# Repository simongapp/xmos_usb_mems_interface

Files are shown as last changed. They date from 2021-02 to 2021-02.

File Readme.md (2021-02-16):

# XMOS USB - MEMS microphone array audio interface
Hardware and firmware files for a MEMS microphones USB audio interface based on the XMOS XUF216. Allows to connect up to  16 microphones and provides the option to cascade multiple base boards.  

This work was done as part of my master's thesis at the TU Berlin, Department of Engineering Acoustics [https://www.akustik.tu-berlin.de/menue/home/parameter/en/](https://www.akustik.tu-berlin.de/menue/home/parameter/en/). The system was evaluated with the Acoular Framework for beamforming [http://www.acoular.org/](http://www.acoular.org/).

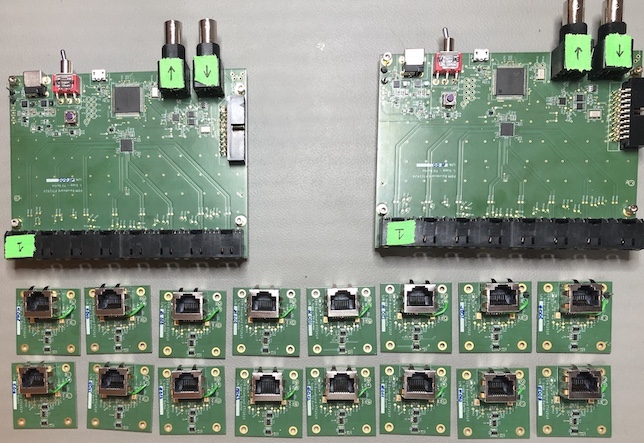
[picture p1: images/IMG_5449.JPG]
  

## Features
- Operates at 48kHz/24bit, with USB 2.0 (UAC2)
- One base board can process up to 16 MEMS microphones
- Cascade multiple baseboards by sharing a word clock or sync to external clock master
- Physically detached microphones, allows to add microphones in pairs of two
- Max. cable length between microphones and base board: 2.5m @ 48kHz
- Impedance matched clock and data transmission lines

## Folders
- 00PCB: EAGLE PCB files for the microphone PCBs and base board
- 01Firmware: XMOS firmware, port documentation and visualizations of the reference code

## Usage
- Clone to your local hard drive

- How to add the firmware files to xTimeComposer (based on https://gist.github.com/ahogen/93bf33ce47bb96c7fda60d844238fa43):  
  1. Link (but don't copy) projects and libraries from SVN dir into workspace
     1. File > Import > General > Existing Projects into Workspace
     2. Choose "Select root directory"
     3. Click "Browse" and navigate to the SVN dir where your projects and libraries were exported
     4. Click "Select All" to choose all projects and libraries
     5. Make sure "Copy projects into workspace" is not checked
     6. Finish

## Known issues
- Data transfer from the microphone boards to the base board leads to inverted data signals on the base board. Fixed by multiplying -1 on the PCM signals.
- No deterministic phase relationship between input and output of the CS2100. This results in a non-deterministic clock shift of up to 162.5ns@48kHz. Considered negligible with respect to the period of audio frequencies from 50ms(20Hz) to 42us(20kHz).
- The current firmware starts audio sampling as soon as the uC is ready, which leads to different buffer sizes and thus a delay of several samples at the host when using multiple base boards. Solution: Synchronize start of audio sampling to first SOF after device configuration. To be implemented in the future.

## License
MIT License

Copyright (c) 2021 Simon Gapp

Permission is hereby granted, free of charge, to any person obtaining a copy
of this software and associated documentation files (the "Software"), to deal
in the Software without restriction, including without limitation the rights
to use, copy, modify, merge, publish, distribute, sublicense, and/or sell
copies of the Software, and to permit persons to whom the Software is
furnished to do so, subject to the following conditions:

The above copyright notice and this permission notice shall be included in all
copies or substantial portions of the Software.

THE SOFTWARE IS PROVIDED "AS IS", WITHOUT WARRANTY OF ANY KIND, EXPRESS OR
IMPLIED, INCLUDING BUT NOT LIMITED TO THE WARRANTIES OF MERCHANTABILITY,
FITNESS FOR A PARTICULAR PURPOSE AND NONINFRINGEMENT. IN NO EVENT SHALL THE
AUTHORS OR COPYRIGHT HOLDERS BE LIABLE FOR ANY CLAIM, DAMAGES OR OTHER
LIABILITY, WHETHER IN AN ACTION OF CONTRACT, TORT OR OTHERWISE, ARISING FROM,
OUT OF OR IN CONNECTION WITH THE SOFTWARE OR THE USE OR OTHER DEALINGS IN THE
SOFTWARE.

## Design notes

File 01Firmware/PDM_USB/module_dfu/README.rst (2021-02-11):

module_dfu
==========

:scope: General Use
:description: module_dfu
:keywords: DFU
:boards: XMOS USB Audio Reference Designes

Code providing firmware upgrade over USB.

./host provides an example of a host application for DFU.  This is written and tested for OSX.  LibUSB is used to aid cross-platform porting.

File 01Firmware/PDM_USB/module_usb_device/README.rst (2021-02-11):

xCORE-USB Device Library
========================

:scope: General Use
:description: Library providing USB-device capabilities on xCORE-USB devices.
:keywords: usb, endpoint

The xCORE-USB Device Library provides support for creating USB devices on the
xCORE-USB family of devices. There are two demonstration applications for using
the library; a HID Class demo and a Custom Class demo.

The Design Guide for more information on using this library to create USB devices.

**Note:** this library can be used with the L-Series but the ``Makefile`` will
need to be modified as described in the Design Guide.

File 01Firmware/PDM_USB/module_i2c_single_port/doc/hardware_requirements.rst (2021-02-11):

Evaluation Platforms
====================

Recommended Hardware
--------------------

This module may be evaluated using the sliceKIT Modular Development Platform, available from digikey. Required board SKUs are:

   * XP-SKC-L16 (sliceKIT L16 Core Board) plus XA-SK-AUDIO plus XA-SK-XTAG2 (sliceKIT xTAG adaptor) plus xTAG-2 (debug adaptor)

Demonstration Application
-------------------------

Example usage of this module can be found within the xSOFTip suite as follows:

   * Package: sc_i2s
   * Application: I2S Master sliceKIT Loop back Demo

The module is used within this application to configure the codec on the Audio sliceCARD.

Hardware Requirements
=====================

This module requires 1K pull-up resistors be present on SCL and SDA externally.

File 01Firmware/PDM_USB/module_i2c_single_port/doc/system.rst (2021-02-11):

Overview 
========

I2C Component provides the ability to write and read I2C based slave devices.
It incorporates features like multimaster capability, clock stretching and clock synchronization.

Components 
----------

i2c master write
++++++++++++++++++++++++

i2c master write component writes the data into i2c slave devices.
 
i2c master read
+++++++++++++++++++++++

i2c master read component read the data from i2c slave devices.

Programming Guide 
=================
 
API (Application Programming Interface)
---------------------------------------

   int i2c_master_wr(int addr, int device, struct i2c_data_info &i2c_data, struct r_i2c &i2c_master);

   This function receives the device address of the slave, the internal address of the slave into which data has to 
   be written, structure containing information about the length of the data and the data itself and the structure 
   containing ports for scl and sda. The device address and the internal address and the data are serially transmitted 
   on sda line.

   int i2c_master_rd(int addr, int device, struct i2c_data_info &i2c_data, struct r_i2c &i2c_master);

   This function receives the device address of the slave, the internal address of the slave from which data has to 
   be read, structure to store the length of received data and the data itself and the structure 
   containing ports for scl and sda.  The device address and the internal address are sent serially and the data received 
   is stored in a structure.

Macros
------

   #define MASTER_TX : if used enables the MASTER Transmit. If commented enables the MASTER receive.

   #define MASTER1 : If used enables the MASTER1 in testbench and if commented disables the MASTER1.

   #define MASTER2 : If used enables the MASTER2 in testbench and if commented disables the MASTER2.

   #define SLAVE1  : If used enables the SLAVE1 in testbench and if commented disables the SLAVE1.

   #define SLAVE2  : If used enables the SLAVE2 in testbench and if commented disables the SLAVE2.

Resource Usage
==============

The following table gives the details of the memory foot print of the functions used.
   
 +----------------+------------------+
 |   function     |   Size(in Bytes) | 
 +================+==================+
 | i2c_master_tx  |       790        |  
 +----------------+------------------+			
 | i2c_master_rx  |       914        |
 +----------------+------------------+
 | i2c_slave_rx   |       584        |    
 +----------------+------------------+ 
 | i2c-slave_tx   |       526        |    
 +----------------+------------------+
 | wait_func      |        74        |
 +----------------+------------------+

Timing Constraints 
==================

I2C Master work at 400Kbps and below.

Validation 
==========
   
Test Bench is provided for testing I2C Master. Both I2C master read and write is tested.
i2C Master is tested for following features

1. Multimaster capability

2. Clock synchronization.

3. Clock stretching.

README.rst file provided guides to setup the simulation environment and the RESULT.rst file gives
the details of tests and the test results.

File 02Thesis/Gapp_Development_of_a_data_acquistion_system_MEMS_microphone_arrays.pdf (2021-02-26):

## berlin

# Masterarbeit Development of a data acquisition system specialized in MEMS microphone arrays

### erstellt von Simon Gapp Matrikel Nr.: 351468

### Erstprufer: Prof. Dr.-Ing. Ennes Sarradj ¨ Zweitprufer: Prof. Giuseppe Caire, Ph.D. ¨

Betreuer: | Dipl.-Ing. Gert Herold
| Dr.-Ing. Andreas Kortke

Technische Universit¨at Berlin, Fachgebiet Technische Akustik Institut fur Str ¨ ¨omungsmechanik und Technische Akustik

17. Dezember 2020

# Erkl¨arung

Hiermit erkl¨are ich, dass ich die vorliegende Arbeit selbstst¨andig und eigenh¨andig sowie ohne unerlaubte fremde Hilfe und ausschließlich unter Verwendung der aufgefuhrten Quellen und Hilfsmittel angefertigt habe. ¨

Berlin, den 17. Dezember 2020

Unterschrift

## Danksagung

Ich m¨ochte mich bei Prof. Sarradj vom Lehrstuhl fur Technische Akustik und bei ¨ Prof. Caire vom Fachgebiet Theoretische Grundlagen der Kommunikationstechnik
fur die M ¨ | ¨oglichkeit, dieses Thema zu bearbeiten zu k¨onnen, herzlich bedanken. Ein
ganz besonderer Dank geht an Gert Herold und Dr. Andreas Kortke fur alle Kom- ¨
mentare, Tipps und Tricks, praktische Unterstutzung sowie die ¨ | ¨außerst prompten
Antworten auf alle meine Anfragen. Weiterer Dank geht an Simon Jekosch fur die ¨ unkomplizierte Urlaubsvertretung und Torsten Daniel fur die handwerkliche Un- ¨
terstutzung beim Messaufbau sowie an das XCore exchange Forum f ¨ | ur alle meine ¨
XMOS Anf¨angerfragen.

1

## Abstract

This thesis describes the design process of a modular Data Acquisition System (DAQ) for Micro-Electro-Mechanical Systems (MEMS) microphone arrays.
Compared to condenser microphones, MEMS microphones come at a significantly lower price, have a smaller footprint, are more resistant towards aging and temperature influences and can contain an integrated Analog-to-Digital Converter (ADC). On the other hand, they have a smaller range with a flat frequency response and usually a lower sensitivity. This results in a lower Signal-to-Noise Ratio (SNR), which can be compensated by increasing the number of microphones and cross-correlating the data in post-processing.
Solutions based on MEMS microphones usually have a fixed array shape with a defined number of microphones. The modular approach of this thesis detaches the Digital Signal Processor (DSP) unit physically from the microphone part, making it possible to adjust the array form at any time. Furthermore, it is possible to cascade multiple DSP units, making the available Universal Serial Bus (USB) bandwidth the limiting factor of the system.

## Zusammenfassung

Diese Arbeit beschreibt den Entwurf eines modularen Data Acquisition System (DAQ) fur Micro-Electro-Mechanical Systems (MEMS)-Mikrofonarrays. ¨
Im Vergleich zu Kondensatormikrofonen sind MEMS Mikrofone deutlich preiswerter, haben einen geringeren Platzbedarf, sind resistenter gegen Alterung und Temperatu-
reinflusse und k ¨ | ¨onnen einen bereits integrierten Analog-to-Digital Converter (ADC)
enthalten. Auf der anderen Seite haben sie einen kleineren Bereich mit einem flachen Frequenzgang und meist eine geringere Empfindlichkeit. Daraus ergibt sich ein geringeres Signal-to-Noise Ratio (SNR), das aber durch eine gr¨ossere Anzahl von Mikrofonen und einer Kreuzkorrelation der Daten in der Nachbearbeitung kompensiert werden kann.
Bestehende L¨osungen, die auf MEMS Mikrofonen basieren, haben meist eine feste Array Form und eine definierte Anzahl von Mikrofonen. Der modulare Ansatz dieser Arbeit trennt die Digital Signal Processor (DSP) Einheit physisch vom Mikrofonteil, sodass eine Anpassung der Array Form jederzeit m¨oglich ist. Daruber hinaus ist es ¨ m¨oglich, mehrere DSP Einheiten zu kaskadieren, wodurch die verfugbare Universal ¨ Serial Bus (USB) Bandbreite zum begrenzenden Faktor des Systems wird.

2

# Contents

Erkl¨arung | 1
Abstract | 2
Zusammenfassung | 2
1 Introduction | 11
2 Operating principles | 14
3 Implementation | 77
4 Results | 103
5 Summary and future work | 124
Bibliography | 129

3

A PCB Files | 135
A.1 Microphone PCB schematics | 135
A.2 Microphone PCB Layout Top | 136
A.3 Microphone PCB Layout Bottom | 137
A.4 Base board schematics | 138
A.5 Base board Layout Top | 146
A.6 Base board Layout Bottom | 147
A.7 Base board Layout Power | 148
B Port Assignments | 149
C Test Points | 151
D CS2100 configuration | 152
E SpectAcoular Code | 153
E.1 Class pdm bb | 154
E.2 Microphone grid | 157
E.3 pdm bb.xml | 159

4

# List of Figures

2.1 Components of a PDM MEMS Microphone | | 15
2.2 Mechanical specifications of a top port MEMS transducer | | 16
2.3 Simplified model of a bottom port MEMS microphone | | 16
2.4 Typical frequency response of a MEMS microphone | | 17
2.5 Analog to digital data converter system | | 19
2.6 Spectrum of a sampling operation | | 20
2.7 Linear quantizer model | | 21
2.8 Quantization error according to the linear model | | 22
2.9 Spectral effect of oversampling | | 23
2.10 Block diagram of a first order Σ∆ ADC | | 24
2.11 Exemplary PDM output and sampled sinus with 64x oversampling . . | 25
2.12 Effect of noise shaping in the Σ∆ modulator | | 26
2.13 CIC decimation filter | | 27
2.14 Exemplary circuit for line termination | | 29
2.15 Exemplary single ended transmission | | 30
2.16 Exemplary differential transmission | | 31
2.17 Setup and hold timing | | 33
2.18 xCore hardware architecture | | 36
2.19 Descriptor relationship | | 47
2.20 Packet Identifier (PID) field | | 49
2.21 Start of Frame (SOF) packet | | 50
2.22 IN, OUT, SETUP packet | | 50
2.23 Data packet structure | | 51
2.24 Retransmission after lost ACK | | 51
2.25 Handshake packet | | 52
2.26 Control Transfer Setup stage | | 54
2.27 Control Transfer Data stage | | 54
2.28 Control Transfer Status stage | | 55
2.29 Isochronous transfer | | 56

5

2.30 Interrupt transfer | | 56
2.31 Bulk transfer | | 57
2.32 bmRequestType field for a SETUP packet | | 58
2.33 Exemplary length of two Configuration Descriptors with wTotalLength 64
2.34 USB Audio device structure using the AC and AS class | | 69
2.35 bmRequestType field for AC requests | | 70
2.36 Comparison of the IAD to the conventional approach | | 76
3.1 Top level view of the system | | 78
3.2 Microphone PCB block diagram | | 79
3.3 Top level view of the base board | | 83
3.4 Clock Generation part of the base board | | 85
3.5 Impedance matching for external clock master | | 88
3.6 Top level view of the main XUF216 tasks | | 88
3.7 Multilayer structure of the used PCB | | 90
3.8 Clock and data path of the system | | 92
3.9 Timing diagram for the base board | | 93
3.10 Core usage and communication between cores | | 95
3.11 Project structure | | 96
3.12 Sixteen count PDM interface | 100
3.13 Frequency response of the decimator | 102
4.1 Manufactured base boards and microphone PCBs | 104
4.2 Measurement setup for a single base board | 105
4.3 Audio master clock on the base board | 106
4.4 Transmitted and received clock signals | 107
4.5 Data signals on the receiving base board | 109
4.6 Setup for the cascaded base board measurement | 110
4.7 Jitter measurement of the 12.288 MHz clocks | 111
4.8 Microphone spacing | 112
4.9 Microphone array layout | 113
4.10 Block diagram of the measurement setup | 114
4.11 Impressions of the measurement | 115
4.12 Measurement positions | 116
4.13 Cross-correlation for adjacent microphones at an incidence angle of 40.5°117
4.14 Frequency response of the microphones normed at 1 kHz | 118
4.15 Delay in samples between base boards, relative to fS = 48 kHz . . . . 120 4.16 Beamforming results. Orange dot: actual source position, pink dot:
estimated position | 122

6

# List of Tables

2.1 Pin assignment of the CAT6/RJ45 connector | | 29
2.2 Default kind for different pointer types | | 42
2.3 USB packet types | | 49
2.4 Setup packet details | | 58
2.5 Standard Requests for USB 2.0 | | 59
2.6 Format of the Device Descriptor | | 61
2.7 Available Languages ID String Descriptor, addressed with ID 0 . . . . | 63
2.8 String Descriptor, addressed from ID 1 and above | | 63
2.9 Configuration Descriptor format | | 65
2.10 Interface Descriptor format | | 66
2.11 Endpoint Descriptor format | | 67
2.12 Standard AudioControl Interface Descriptor | | 71
2.13 AudioControl Interface Header Descriptor | | 72
2.14 AudioControl Clock Source | | 72
2.15 Input Terminal Descriptor | | 73
2.16 Feature Unit Descriptor | | 74
2.17 Standard AudioStreaming Interface Descriptor | | 75
2.18 Class specific AudioStreaming Interface Descriptor | | 75
2.19 Interface Association Descriptor format | | 76
3.1 Current estimation of the system, measured values in brackets . . . . | 78
3.2 Current estimation for the microphone PCB, measured value in brackets 81
3.3 Sparrow limit of the validation array | | 81
3.4 Current estimation for the base board, measured value in brackets . . | 84
3.5 Mandatory components of the XMOS USB subsystem [68] | | 94
3.6 Core usage on Tile 0 | | 94
3.7 Core usage on Tile 1 | | 94
3.8 Description of used modules and libraries | | 96

7

4.1 Microphone PCB positions and corresponding IDs | 112
4.2 Measurement positions | 116
4.3 Used beamformer parameters | 121
4.4 Angular difference between the actual and calculated source position
for a delay of 10 sample | 123

8

## List of abbreviations

AC AudioControl

ACK Acknowledgement

ADC Analog-to-Digital Converter

AoIP Audio over IP

AOP Acoustic Overload Point

AS AudioStreaming

ASIC Application Specific Integrated Circuit

AVB Audio Video Bridging

CIC Cascaded-Integrator-Comb

COTS Commercial off-the-shelf

CRC Cyclic Redundancy Check

CS Control Selector

DAC Digital-to-Analog Converter

DAQ Data Acquisition System

dB Decibel

dBFS Decibel Full Scale

dBSPL Decibel Sound Pressure Level

DC Direct Current

DFU Device Firmware Upgrade

DMA Direct Memory Access

DSP Digital Signal Processor

ECL Emitter-coupled Logic

EMF Electromagnetic field

EOP End of Packet

ESD Electro Static Discharge

FFT Fast Fourier Transformation

FIFO First in, First out

FIR Finite Impulse Response Filter

FPGA Field-Programmable Gate Array

FU Feature Unit

GPIO General Purpose Input Output

GUI Graphical User Interface

HID Human Interface Device

HPF High-Pass Filter

ID Identifier

I/O Input/Output

IAD Interface Association Descriptor

IBN In-Band Noise

IC Integrated Circuit

IDE Integrated Development Environment

IFFT Inverse Fast Fourier Transformation

IIR Infinite Impulse Response Filter

9

ITD Input Terminal Descriptor

LDO Low Drop-out

LLVM Low Level Virtual Machine

LPF Low-Pass Filter

LSB Least Significant Bit

LVDS Low Voltage Differential Signaling

MEMS Micro-Electro-Mechanical Systems

MIPS Million Instructions Per Second

MIPS Million Instructions per Second

MSB Most Significant Bit

NRZI Non-return-to-zero, inverted

NTF Noise Transfer Function

OSR Oversampling Ratio

PCB Printed Circuit Board

PCM Pulse-Code Modulation

PDF Probability Density Function

PDM Pulse-Density Modulation

PECL Positive Emitter-coupled Logic

PHY Physical Layer

PID Packet Identifier

PLL Phase-Locked Loop

PSD Power Spectral Density

PSU Power Supply Unit

PTP Precision Timing Protocol

RTOS Real-Time Operating System

S-FTP Screen Foiled Twisted Pair

SHARC Super Harvard Architecture Single-Chip Computer

SNR Signal-to-Noise Ratio

SOF Start of Frame

SPST Single Pole Single Throw

STF Signal Transfer Function

THD Total Harmonic Distortion

TP Test Point

TSN Time Sensitive Networks

UAC1 Universal Serial Bus (USB) Audio Class 1.0

UAC2 USB Audio Class 2.0

USB Universal Serial Bus

VHDL Very High Speed Integrated Circuit Hardware Description Language

XUD XMOS USB Device Driver

10

# Chapter 1

# Introduction

A microphone array consists of several microphones placed in different locations. Typical applications of microphone arrays are speech extraction in noisy environments [1, 2] or source localization [3] often in combination with noise measurements [4]. Noise measurement applications usually consist of a larger number of microphones compared to speech extraction applications. Since the focus of this thesis is on a larger number of microphones, the introduction to this topic will be explained using examples from the field of noise measurements based on [5].
Typical measurement scenarios are in wind tunnels, during aircraft overflights and engine noise tests.
Depending on the goal of the measurement, various parameters can be adjusted, which are presented below.
The Signal-to-Noise Ratio (SNR) and the spatial resolution are defined by the microphone count. In general, it can be said that an increased number of microphones increases both, the SNR and the spatial resolution. The dynamic range, the frequency range and the sensitivity can be roughly approximated by the dimensions of a microphone. As a rule of thumb, it can be said that smaller microphones can measure higher frequencies compared to a larger microphone that usually has a higher sensitivity. The most accurate results can be achieved if the Data Acquisition System (DAQ) samples all microphones coherently.
Arranging the microphones in spirals or several circles with an odd number of regularly spaced microphones seems to give the best results.
Considering all hardware requirements, adequate results depend on the chosen algorithm. In general, the selection of the most suitable algorithm is a trade-off between spatial resolution, dynamic range and computational effort.

11

Microphone arrays based on Micro-Electro-Mechanical Systems (MEMS) microphones provide a cost-effective alternative to established systems based on condenser microphones. Advantages of the MEMS technology are a small footprint, low cost and a high resistance to aging and temperature influence. The microphones have, on the other hand, a smaller area with a flat frequency response due to their physical design and a lower SNR.

Commercially available arrays with up to 16 microphones are provided by [6, 7, 8]. Larger arrays are commercially available from [9]. Research projects on large scale arrays can be found in [10, 11, 12].
This thesis distinguishes between different processing stages with the terms preprocessing and post-processing. Preprocessing describes the conversion of the raw microphone signals into suitable signals for post-processing. Post-processing describes the application of an algorithm to evaluate the preprocessed microphone signals. All works presented apply preprocessing in a Digital Signal Processor (DSP) which is either a specialized microcontroller, a Field-Programmable Gate Array (FPGA) or an Application Specific Integrated Circuit (ASIC). In most of the works presented, post-processing is carried out on the same platform on which the preprocessing is performed.

A modular system is designed in this thesis in which the microphones are separated from the processing unit. The preprocessing is performed in the processing unit, while the post-processing is performed on an external device. The system consists of two physically separate units: the base board, which contains the processing unit as well as the peripherals necessary for its operation, and microphone Printed Circuit Boards (PCBs), which contain two microphones each as well as some peripherals necessary for their operation.
The term modular describes two aspects: Firstly, the possibility of operating a variable number of microphones with one processing unit and, secondly, the possibility of operating several processing units with the same clock signal for audio sampling. This overcomes the limitation of the ability to use only a single processing unit and the available transmission bandwidth becomes the limiting factor. Furthermore, the shape of the microphone array can be adjusted at any time.
In this thesis the following questions are evaluated:
- Does the modular system provide sufficiently accurate data for post-processing?
- Is it feasible to physically detach the microphones from the DSP?
- Is the selected transmission protocol suitable for transferring the array data?

12

## 1.1 Chapter overview

This thesis is divided into five chapters, covering the theoretical principles, the description of the design process and the subsequent validation of the developed system. It concludes with a summary of the work and presents suggestions for future implementations. The chapters are structured as follows:

Chapter 1 Introduces the topic and presents the research questions.

Chapter 2 Presents the operating principles of the microphones used and describes the review process for a suitable processing unit. Subsequently, details on the architecture of the selected processing unit are described. A further chapter is dedicated to the transmission protocol between a host and the processing unit and deals with the specific parts of the Universal Serial Bus (USB) protocol used in this work.

Chapter 3 Describes the implementation process for the hardware and the firmware.

Chapter 4 Provides details on the validation process of the system from an electrical and acoustic point of view.

Chapter 5 Summarizes this thesis, presents an answer to the research questions and provides suggestions for future implementations.

13

# Chapter 2

# Operating principles

This chapter presents the operating principles of the hardware and firmware that is used in this thesis. It is structured as follows: Sec. 2.1 reviews the principles that are used in a Micro-Electro-Mechanical Systems (MEMS) transducer. In Sec. 2.2, a brief review of the applied transmission techniques are presented. Sec. 2.3 describes the selection process of a suitable processing unit and Sec. 2.4 describes the architecture of the selected unit in more detail. Lastly, Sec. 2.5 summarizes the relevant parts of the selected Universal Serial Bus (USB) protocol.

## 2.1 Data acquisition

The used microphones are based on the MEMS technology. As illustrated in Fig. 2.1, the two main components of the microphone are a MEMS transducer and a Σ∆ Analog-to-Digital Converter (ADC). Components other than the MEMS transducer are summarized below by the term Application Specific Integrated Circuit (ASIC).

### 2.1.1 Micro-Electro-Mechanical Systems transducer

This section describes the MEMS transducer principles based on [13, 14]. The transducer can be described as a silicon capacitor consisting of two plates. While one plate is at a fixed position, the other plate is moving accordingly to the pressure change caused by a sound wave. One could describe the MEMS transducer as a capacitor with variable capacitance. The capacitance of a plate capacitor is calculated as follows:

C = ε0εr

A
d

(2.1)

14

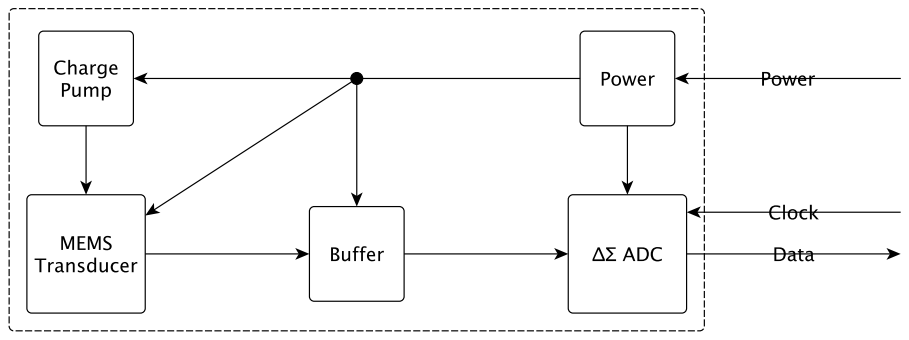
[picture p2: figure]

Figure 2.1: Components of a PDM MEMS Microphone, Figure from [13]

With A: Plate surface, d: Distance between plates, ε0: vacuum permittivity and εr: relative permittivity. By changing the distance of the two plates, a change in capacity is achieved, which results in a change in voltage:

U =

Q
C

(2.2)

With U: voltage, Q: charge and C: capacitance. The voltage change is detected by the buffer between the transducer and the Σ∆ ADC.

The mechanical specification for a top port MEMS microphone is depicted in Fig. 2.2. Sound waves enter from the top and pass the acoustic holes. The change in pressure causes the membrane to move, which eventually leads to a change in the capacitance of the transducer. This leads to a change in the charge of the capacitor plates, changing the input voltage at the ASIC.
Fig. 2.3 depicts a simplified model of a bottom port MEMS microphone with the ASIC and the enclosure. A bottom port microphone is also used in this thesis. The back volume is defined by the dimensions of the enclosure and the components placed inside, while the front volume is defined by the dimensions of the underlaying substrate.

15

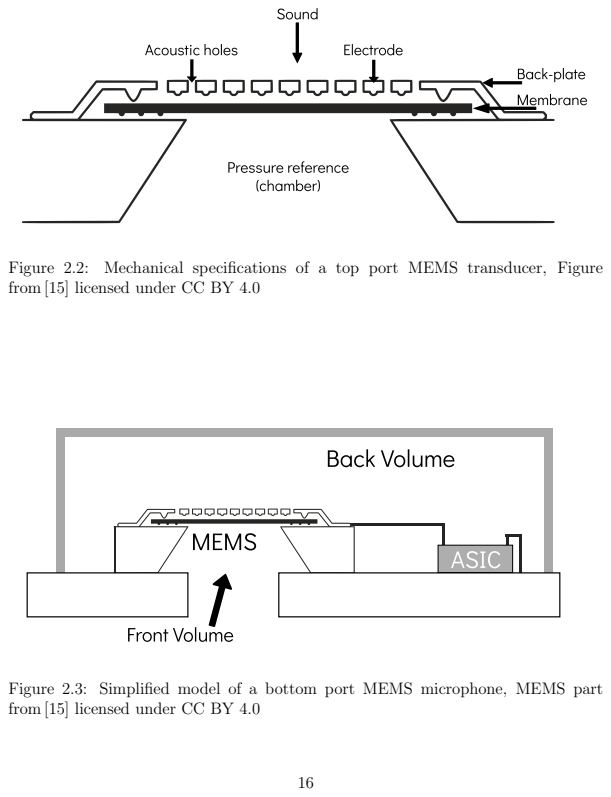
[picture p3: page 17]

Figure 2.2: Mechanical specifications of a top port MEMS transducer, Figure
from [15] licensed under CC BY 4.0

Figure 2.3: Simplified model of a bottom port MEMS microphone, MEMS part

The typical frequency response of a MEMS microphone as shown in Fig. 2.4. Two areas show a larger deviation from a flat frequency response: In the low frequency range from 10 Hz to 200 Hz and in the high frequency range above 10 kHz.

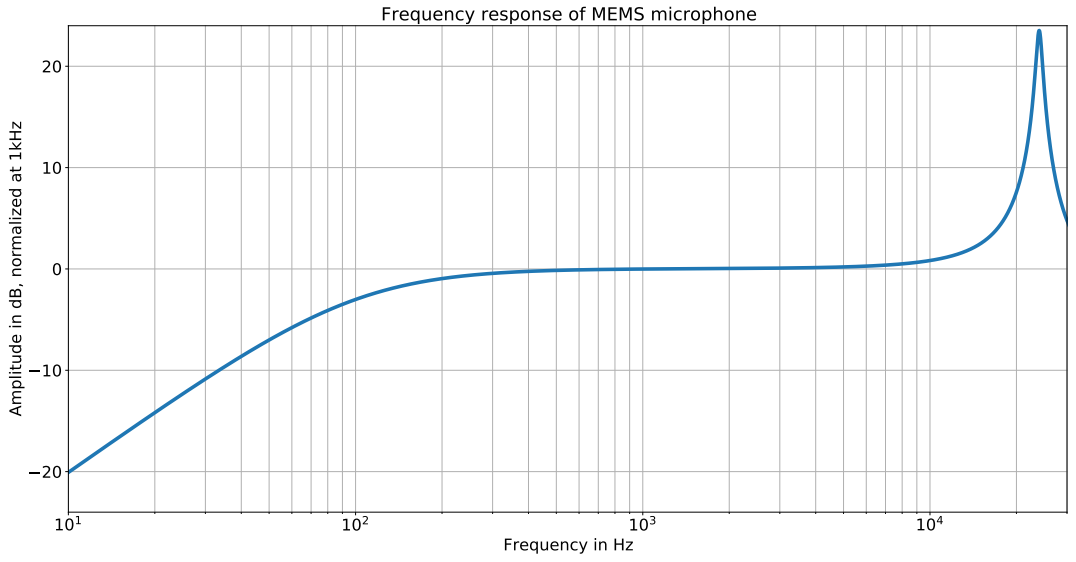
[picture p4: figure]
Frequency in Hz; Amplitude in dB, normalized at 1kHz; Frequency response of MEMS microphone

Figure 2.4: Typical frequency response of a MEMS microphone, Figure from [13]

These deviations are defined by the physical properties of the microphone. The main parameters are the form and size of the ventilation hole, the front chamber geometry and the back chamber geometry. It can be assumed that the ASIC has a flat frequency response.
While the attenuation at low frequencies is influenced by the geometry of the ventilation hole and the back chamber geometry, the gain at high frequencies is only influenced by the geometry of the front chamber. The high frequencies are amplified by a resonance peak caused by the Helmholtz effect. This effect describes the air resonance in a cavity. The resonance frequency is approximated as follows: [16]:

fR ≈

c
2π

r
S

V · Leff

(2.3)

With c: speed of sound, S: cross-section of the neck, V : volume of the back chamber and Leff: effective length of the neck which uses a correction factor of ∆l = 0.85r, with r: radius of the tube. The correction factor takes the effects at an open flange tube into account.

17

This approximation does not account for effects such as thermal-viscous and acoustic impedances and other material-related influences. Therefore, an approximate calculation of the resonance frequency for the microphone used is omitted.

### 2.1.1.1 Acoustic parameters

A microphone can be described with the following parameters:

Sensitivity The sensitivity of a digital microphone describes a percentage of the full scale output that is generated at 94 dBSPL. The value is given in Decibel Full Scale (dBFS) where the maximum value describes the highest signal level that can be output by the microphone. It is calculated as follows [17]:

SensitivitydBFS = 20 · log10 Sensitivity%FS

OutputDREF
(2.4)

With OutputDREF = 1.0. There is no relation between the digital output in dBFS and an analog output in dBV. The analog output is referenced to 1 VRMS while the digital output is referenced to the digital full scale.

Directivity The directivity of a microphone describes the variation of the sensitivity response with respect to the direction of arrival of the sound [14]. The MEMS transducer used is a pressure transducer and has an omnidirectional characteristic. This means that the sensitivity is independent from the location of the sound source and therefore identical for all locations.

Signal-to-Noise Ratio The Signal-to-Noise Ratio (SNR) specifies the ratio between a given reference signal (usually 1 kHz at 94 dBSPL) to the amount of residual noise at the microphone output [14].
The main contributor of the noise is the MEMS sensor while the noise of the ASIC can be neglected. The SNR is specified in Decibel (dB) and calculated as follows [18]:

SNR = 10 · log10

PSignal

PNoise

[dB] | (2.5)

Dynamic range The dynamic range describes the difference between the minimum and maximum signal the microphone is able to generate as an output. While the minimum signal describes the signal distinctive from residual noise, the maximum audio signal is described by the microphone output with 10 % Total Harmonic Distortion (THD) at 1 kHz. This point is known as Acoustic Overload Point (AOP).

18

### 2.1.2 Analog to digital conversion

The description of the analog to digital conversion is based on [18]. The basic principles of the analog to digital conversion can be separated into two main tasks:

- Uniform sampling in time
- Uniform quantization in amplitude

Fig. 2.5 depicts the main components of an ADC. It consists of three operating blocks: an antialiasing filter, a sample and hold block and a quantizer.

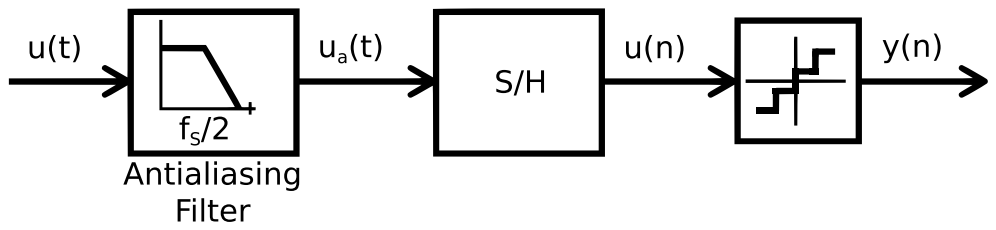
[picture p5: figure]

Figure 2.5: Analog to digital data converter system, Figure from [18]

With the following assumptions, it can be said that sampling in time is a completely invertible process: The signal information of the continuous input waveform u(t) is contained in the signal band |fsig| ≤ fB where fB is defined as the signal bandwidth. The input signal is sampled at uniform time intervals TS or with a fixed frequency fS, resulting in a periodicity of the original spectrum at multiples of fs. This is illustrated in Fig. 2.6.
The periodization arises from the sampling process which is considered as a multiplication of the input signal u(t) with a train of Dirac pulses spaced at 1/fs in the time domain or the convolution of the signal spectrum with a periodic train of Dirac pulses spaced at fs in the frequency domain. It can be seen in Fig. 2.6 that the original baseband spectrum can be reconstructed if the Nyquist theorem is fulfilled:
fs ≥ 2 · fB = fN | (2.6)

with fN as Nyquist frequency. This avoids overlapping and aliasing of the baseband. To only convert the bandwidth defined in Eq. 2.6, an antialiasing filter precedes the ADC.

19

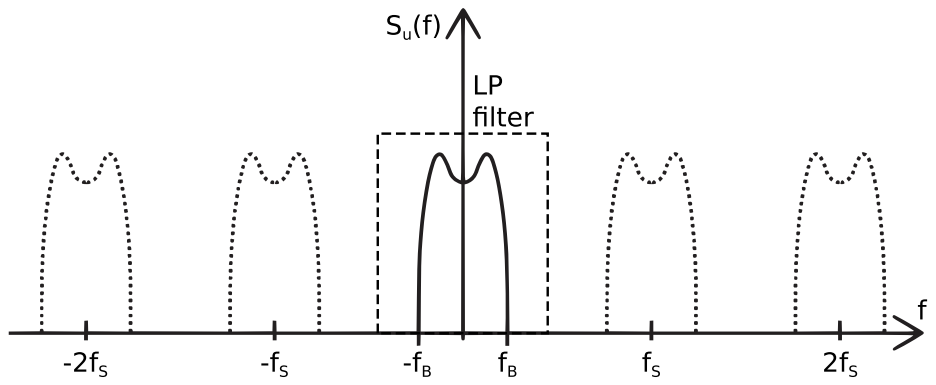
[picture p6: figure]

Figure 2.6: Spectrum of a sampling operation, Figure from [18]

Operating an ADC at the Nyquist frequency would result in zero transition band for the antialiasing filter to cut-off unwanted frequencies in the baseband.
Filters with a gentle roll-off are easier to design with the advantage that they require less power and introduce less phase distortion. Therefore, many ADCs work with sampling rates higher than fN . This is known as oversampling, hence the name oversampling ADCs. The Oversampling Ratio (OSR) is defined as:

OSR = fs 2 · fN
(2.7)

Converting a continuous range of analog values into a set of discrete levels is called quantization. This is a non-invertible process, since an infinite number of input amplitude values of the sampled analog signal u(n) are mapped into a finite number of output amplitude values. Even an ideal quantizer introduces an error into the output of the ADC.
The key characteristic of a quantizer is the number of Bits Bint which correlate to the different output levels. Mapping the analog input to 2Bint discrete output levels describes the resolution of the quantizer in terms of Bint-bits.
Assuming equally spaced levels, the quantizer operation is called uniform and has the following step width:

∆ = F S
2

Bint − 1

(2.8)

with F S: full-scale output range. The valid quantizer input range is from ±F S/2 which is quantized into 2Bint different output levels, encoded into a binary digital

20 representation. The resulting quantization error is defined as the difference between the input signal and the output signal.
The gain of a single bit quantizer is not exactly defined as well as the quantization error itself. Assuming the input changes rapidly from sample to sample by amounts larger than the step size ∆, then the quantization error appears uncorrelated and has an equal probability of lying anywhere in the range of [−∆/2, ∆/2]. This makes the assumption possible that the quantization error can have statistical properties. These properties define the basis of the additive white noise model of the quantizer which states that
- the quantization error can be expressed as a random variable.
- there is no correlation between the quantization error sequence e(n) and the input q(n).
- over the range [−∆/2, ∆/2], the Probability Density Function (PDF) of the quantization error process pdfe

is uniform.

- the Power Spectral Density (PSD) of the quantization error process Se(f) is flat

The linearized quantizer model is shown in Fig. 2.7. It represents the Input/Output (I/O) characteristics of the quantizer: a gain kq and a quantization error e(n).

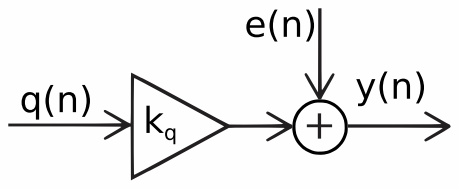
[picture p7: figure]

Figure 2.7: Linear quantizer model, Figure from [18]

These assumptions convert the deterministic nonlinear system into a stochastic linear system with the quantization error described as quantization noise. The total quantization noise power can be calculated from Fig. 2.8(a) as follows:

σ

2
e =

Z ∞

−∞

e

2
pdfe∂e =

∆²
12

(2.9)

21

It is independent from the sampling frequency and is only determined by the quantizer resolution. The signals at the quantizer are sampled signals, which causes all quantization noise power σ

2
e

to be folded into the frequency range of [−fS/2, fS/2]. Using white noise as an approximation (compare to Fig. 2.8(b)) results in the PSD of the quantizer being:

Se(f) = ∆²
12

1
fS

(2.10)

This means that the PSD reduces proportionally with an increased sampling frequency.

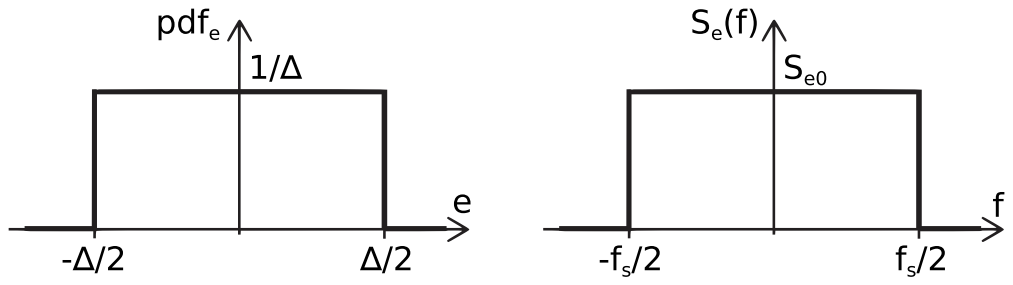
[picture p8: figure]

(a) Probability density function | (b) Power Spectral Density (PSD)

Figure 2.8: Quantization error according to the linear model, Figure from [18]

A digital low-pass filter follows the oversampled converter and eliminates all parts outside the in-band range, also leaving only a small part of the total quantization noise. The In-Band Noise (IBN) can be described as:

IBNOSR =

# Z fB

−fB

Se(f)df =

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
OSR | (2.11)

The maximum SNR of the ADC is described by the ratio between the corresponding input signal power PFS/2 and the IBN:

SNROSR = 10 · log10
PFS/2

IBNOSR
(2.12)

= 6.02 · Bint + 10 · log10 OSR + 1.76[dB]

Every doubling of the OSR increases the resolution by 3 dB or approx. 0.5 bit. The advantage of an increased OSR is depicted in Fig. 2.9.

22

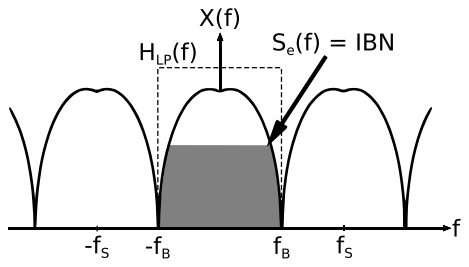
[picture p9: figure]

(a) Quantization and in-band noise for OSR=1

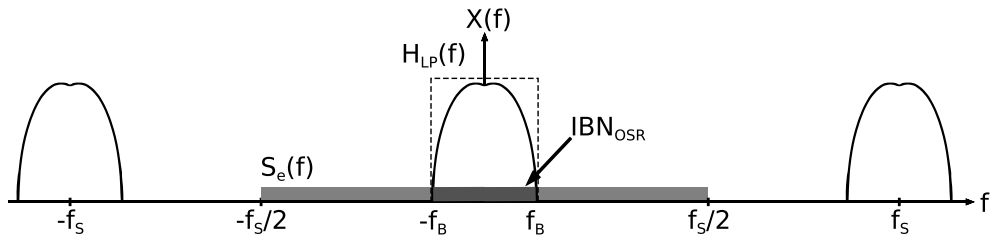
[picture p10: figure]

(b) Quantization and in-band noise for OSR=4

Figure 2.9: Spectral effect of oversampling, Figure from [18]

All theory until now was based on a purely open-loop controlled system. This means that the output signal is steered by an input signal and affected by noise introduced through the conversion process.

### 2.1.2.1 Σ∆ modulation

By introducing a feedback path to the system, a closed control loop is achieved. This makes it possible to implement different transfer functions and divide the output into a Signal Transfer Function (STF) and Noise Transfer Function (NTF).
In an ideal system, the configuration of the STF and the NTF leads to a complete cancelation of the noise inside the desired signal bandwidth, with the signal itself being unaffected. Outside the bandwidth of interest, the NTF gain can be high while the STF gain can be low.

NTFideal = STFideal =

(
0, −fB ≤ f ≤ fB
1, else

(2.13)

23

It is shown in Eq. 2.13 that the ideal STF is described by an ideal Low-Pass Filter (LPF), while the ideal NTF is described by an ideal High-Pass Filter (HPF) with the cut-off frequency being at least at fB. This results in the quantization noise being shaped away from the bandwidth of interest, leading to a noise shaping converter. The block diagram of a first order noise shaping converter is depicted in Fig. 2.10. Higher order noise shaping converters contain multiple integrator stages in the Σ∆ modulator block, which mainly increases the SNR.

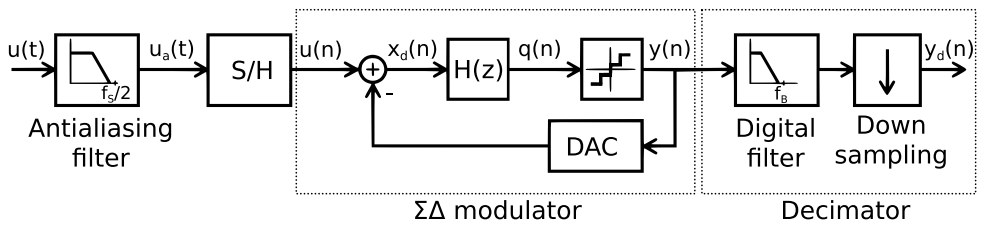
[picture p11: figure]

Figure 2.10: Block diagram of a first order Σ∆ ADC, Figure from [18]

A noise shaping converter consists of the following parts:

- Antialiasing Filter: The antialiasing filter eliminates spectral components above fs/2 which leads to a band limited input for the modulator. This filter ensures that the subsequent sampling operation does not alias input signals from higher frequencies into the band of interest
- Sample and Hold: The sample and hold block performs a track and hold operation. The function of this block can be described best as a clocked switch that charges a capacitance with the input for half of the clock period and transfers this voltage level from the capacitor to the Σ∆ modulator during the other half of the period. Eventually, it is interpreted by the quantizer.
- Σ∆ modulator: This block performs the actual analog to digital conversion by quantizing the input signal. Furthermore, the quantization error from the internal quantizer is moved out of the band of interest. The quantizer is typically implemented with a low resolution and the internal feedback Digital-to-Analog Converter (DAC) has the same resolution, thus not introducing additional error to the system. The output of the Σ∆ modulator is a Pulse-Density Modulation (PDM) signal.
A simulation of a sinusoidal input to a Σ∆ modulator is shown in Fig. 2.11. It

24 was created with the Delsig Toolbox [19] and shows that the density of zeros and ones is determined by the amplitude of the sine wave.

- Decimator: The decimation filter contains a digital low-pass filter to eliminate all noisy out of band components and performs the downsampling operation. A detailed description of the decimation process is presented in Sec. 2.1.2.2.

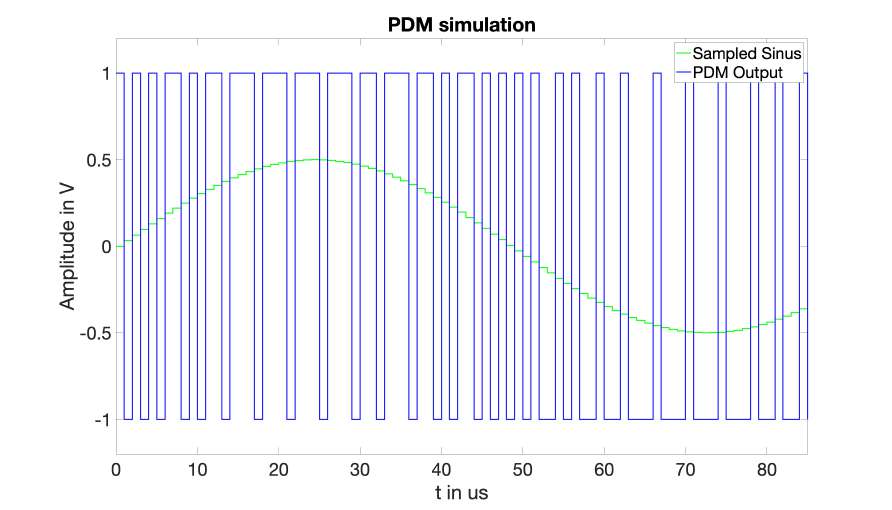
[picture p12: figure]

Figure 2.11: Exemplary PDM output and sampled sinus with 64x oversampling

Replacing the quantizer in Fig. 2.10 with the linearized quantizer model from Fig. 2.7 results in a linearized Σ∆ modulator with the following transfer function:

Y (z) = STF(z)U(z) + NTF(z)E(z) | (2.14)

with

STF(z) = 1

1
H(z)kq

+ 1

, NTF(z) = 1
1 + H(z)kq

(2.15)

and U(z): input signal, Y (z): output signal, U(z): quantization error.
The easiest filter for H(z) is a first order integrator described by the following transfer

25

function:

I(z) = z

−1
| 1 − z

−1

(2.16)

For low frequencies, the linearized Σ∆ modulator from Eq. 2.15 becomes:

STF(z) = z

−1
, NTF(z) ≈

1 − z

−1
kq

(2.17)

The effect of the high-pass filtered noise of the NTF is shown in Fig. 2.12. It is clearly visible that most of the noise is shaped out of the band of interest.

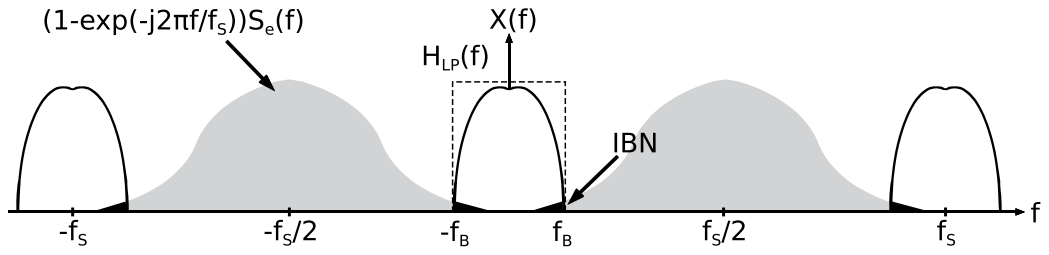
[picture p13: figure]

Figure 2.12: Effect of noise shaping in the Σ∆ modulator, Figure from [18]

The IBN can be approximated as follows:

IBN ≈

# Z fB

−fB

∆²
12fs

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
df | (2.18)

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
qOSR³

Increasing the oversampling ratio decreases the IBN power by 9 dB per octave. The corresponding SNR is approximated as follows:

SNR = 10 · log10
PSig
IBN1
∼ 10 · log10

OSR³
[dB] | (2.19)

This corresponds to 1.5 bit increase in resolution for doubling the OSR.

26

### 2.1.2.2 PDM to PCM conversion

For further signal processing the PDM signal from the Σ∆ modulator is converted into a Pulse-Code Modulation (PCM) signal which is suitable for post-processing. The two signal types are distinguished by their sampling rate and their bit-depth. The PDM signal has a high sampling rate and a low bit depth, while the PCM signal has a low sampling rate and a high bit-depth.
The decimation from a high sampling frequency to a low sampling frequency is performed by a Cascaded-Integrator-Comb (CIC)-Filter [20]. The filter structure is shown in Fig. 2.13. The filter is divided into two different structures: The integrator

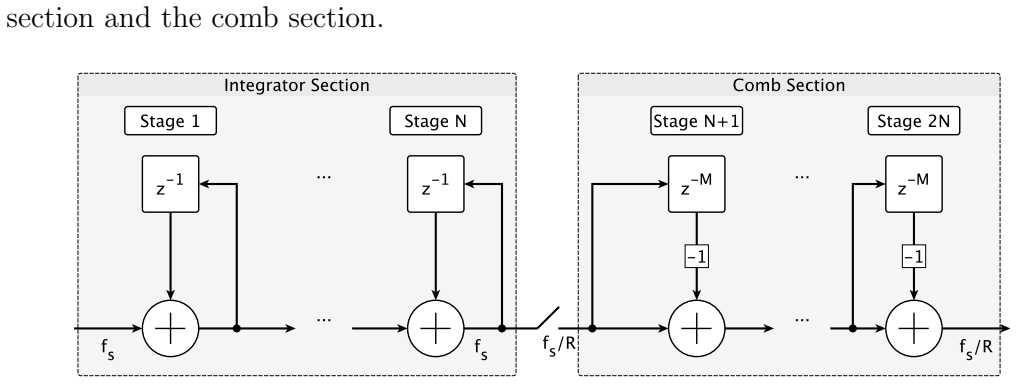
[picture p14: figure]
section and the comb section.

Figure 2.13: CIC decimation filter, Figure from [20]

The integrator section consists of N ideal digital integrator stages which operate at the high sampling frequency fS. Each stage is implemented as a one-pole filter with a unity feedback coefficient. The transfer function for a single integrator stage is [20]:

HI (z) = 1
1 − z

−1

(2.20)

The comb section operates at the low sampling rate fS/R. The integer R describes the rate change factor . The section consists of N comb stages with a differential delay of M samples per stage. This parameter is used to control the frequency response of the filter. The transfer function for a single comb stage is [20]:

HC(z) = 1 − z

−RM | (2.21)

The switch between the two stages subsamples the output of the last integrator stage. This reduces the sampling rate from fS to fS/R. The transfer function for

27 the complete CIC-Filter is [20]:

H(z) = H

N
I

(z)H

N
C (z) =
1 − z

−RMN

(1 − z

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
(2.22)

With R: Input sampling rate to output sampling rate ratio, M: number of samples per stage (usually 1 or 2) and N: Number of stages in the CIC-Filter.
Eq. 2.22 shows that the CIC-Filter is functionally equivalent to a cascade of N uniform FIR filter stages. This shows the advantage of the filter structure: The CIC-Filter does not need a multiplication unit since there are no coefficients other than ±1 which can be easily processed with a signed binary representation. Furthermore, it uses limited storage which results in a very economic hardware implementation. The frequency response is fully determined by the parameters R, M and N which limits the range of filter characteristics. It is recommended to use conventional filter structures to shape the frequency response after the CIC-Filter in the lower sampling rate domain where the number of multiplications per second is low.

The analog to digital conversion that is used in this project is divided into two stages. The MEMS microphone contains the Σ∆ modulator and sends the modulated data to the Digital Signal Processor (DSP) unit. In the DSP unit, the decimation of the signal is performed. This approach allows to specify the bit depth and sampling rate of the decimated PDM signal at runtime.

## 2.2 Data transmission

The microphones are physically separated from the processing unit. To ensure reliable transmission of the signals, the propagation velocity of the signals and the delay caused by the components used must be taken into account. This limits the maximum distance between the microphones and the processing unit.
The clock and data transmission are carried out over a distance of 2 m. In order to make the transmission reliable and less susceptible to external influences, the Low Voltage Differential Signaling (LVDS) principle is used for all transfers between the Printed Circuit Board (PCB)s.

28

All transmissions utilize CAT6 Screen Foiled Twisted Pair (S-FTP) cables with RJ45 connectors. CAT6 cables are affordable Commercial off-the-shelf (COTS) products. The cables have four twisted pairs with an impedance of 100 Ω. The cut-off frequency is at 250 MHz and the shielding is improved because each twisted pair has its own shield. The pin assignment is shown in Tab. 2.1

No | Pair | Signal
1 | 3 | Microphone 2 Data N
2 | 3 | Microphone 2 Data P
3 | 2 | Clock P
4 | 1 | GND
5 | 1 | 5 V
6 | 2 | Clock N
7 | 4 | Microphone 1 Data P
8 | 4 | Microphone 1 Data N
Table 2.1: | Pin assignment of the
CAT6/RJ45 connector

### 2.2.1 Transmission line termination

In an ideal transmission line model, a wave would propagate to infinity. In the real world the transmission line has an end where the propagating wave encounters a load resistance RL. Consider a circuit with a voltage source uS, an output resistance RS and a load resistance RL as shown in Fig. 2.14. The arrows in the signal path indicate the transmission distance between source and load.

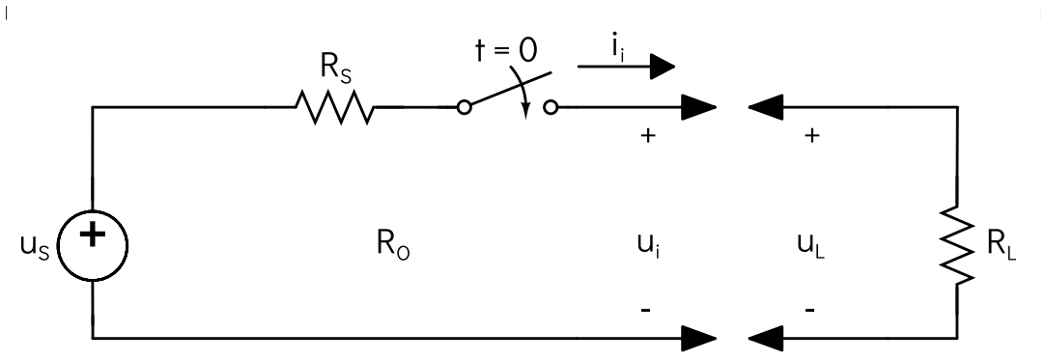
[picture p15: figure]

Figure 2.14: Exemplary circuit for line termination, Figure from [21]

The conservation of energy principle leads to [21]:

Pi = PL + Pr | (2.23)

29

where:

Pi =

u

2
i
RO

(2.24)

PL =

u

2
L
RO

(2.25)

Pr =

u

2
r
RO

(2.26)

With Pi

: input signal power, PL: load power and Pr: power not absorbed by the load and reflected back into the transmission line. Inserting Eq. 2.24ff. into Eq. 2.23:

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
(2.27)

⇔

ur
ui

=

RL − RO
RL + RO
= ρvL | (2.28)

With ρvL as the voltage reflection coefficient.
Eq. 2.28 shows that the voltage reflection coefficient equals zero if RL = RO. A value of 1 indicates a complete reflection of the wave, while a value smaller than 0 indicates a mismatch between the load and output impedance.

### 2.2.2 Single ended and differential transmission

Single ended transmission A signal transmission over a single line is called single ended transmission. An example is shown in Fig. 2.15.

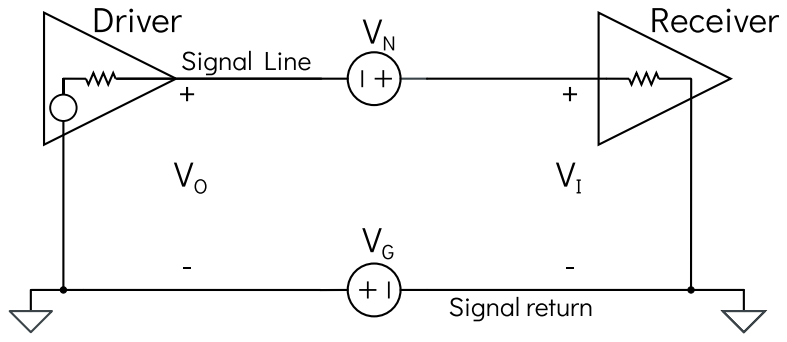
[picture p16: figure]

Figure 2.15: Exemplary single ended transmission, Figure from [21]

30

A sender and receiver share a common ground path. The input of the receiver is interpreted with respect to the ground level. The receiver input is calculated as follows [21]:

VI = VO + VN + VG | (2.29)

With VI : input voltage at the receiver, VO: output voltage at the driver, VN : noise source for high frequency electromagnetic coupling and VG: noise introduced by changes in the ground current. As it can be seen in Eq. 2.29, the transmitted signal is susceptible to noise sources in the transmission line.
The advantages of a single ended transmission are its simplicity and low cost of implementation. The disadvantages are a poor noise performance at high signaling rates or long distances. This is mainly because the noise coupled into the circuit adds to the signal voltage.

Differential transmission A differential signal transmission describes a transmission with complementary outputs. An example is illustrated in Fig. 2.16.

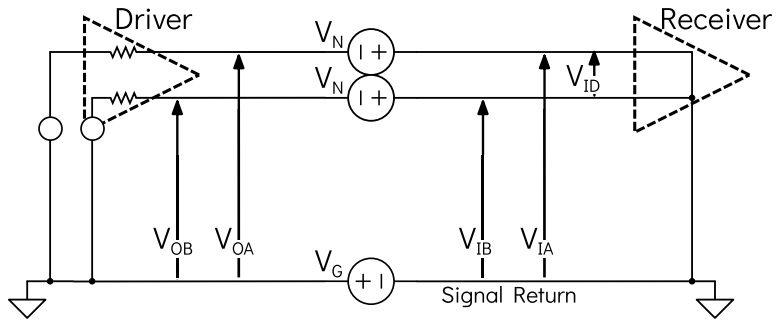
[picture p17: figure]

Figure 2.16: Exemplary differential transmission, Figure from [21]

The difference to the single ended transmission is that the receiver detects the voltage difference between the complementary input signals. The input at the receiver is defined as follows [21]:

VIA = VOA + VN + VG | (2.30)
VIB = VOB + VN + VG | (2.31)
VID = VIA − VIB | (2.32)
= VOA + VN + VG − (VOB + VN + VG)

= VOA − VOB

31

As it can be seen in Eq. 2.32, the common noise terms are canceled out due to the difference detection between the two signals rather than detecting a difference to a common reference point. It can be assumed that the differential signal pairs are exposed to the same noise sources, since they usually are close together.
Twisting signal pairs together ensures similar exposure to the noise sources and cancels out the Electromagnetic field (EMF) from magnetic field coupling by reversing the polarity in adjacent loops created by the twist.
Furthermore, differential circuits radiate substantially less noise than single-ended circuits. The complementary currents in each transmission line cancel out the field generated by the other transmission line.
A disadvantage of the differential signaling is the increased cost and complexity in the circuitry as well as in the silicon.

Low Voltage Differential Signaling LVDS is a standard that specifies electrical characteristics of a differential signal transmission. It is optimized for low power consumption and moderate transmission speeds.
A driver provides 350 mV nominal into a 100 Ω load [22]. This results in a power consumption (from Eq. 2.24) of Pi =

u

2
i
RO

=

350 mV²
100 Ω = 1.225 mW. The transmissions are specified for data transfers up to 1 Gbit/s for a length up to 10 m. For higher data transmission rates, principles like Emitter-coupled Logic (ECL) or Positive Emitter-coupled Logic (PECL) are suitable but consume considerably more power.

### 2.2.3 Timing limitations

The PDM output of the microphones is read by the processing unit on the rising edge of the clock. This requires the microphone output to reach a stable point (either a digital zero or a digital one) before the rising edge of the clock and to hold this value for a certain time until the next value of the output is set on the data line which introduces two phases:
The setup phase tsu describes the time before the rising edge of the clock signal where the data is already valid. The hold phase th describes the time after the rising edge of the clock, where the data is still valid. Outside these two phases, there is no guarantee that the data is valid. The principle is depicted in Fig. 2.17.

32

tsu th

## Clock

Data | valid

Figure 2.17: Setup and hold timing [23]

## 2.3 Review of available processing units

The processing units range from small scale commercially available processors to Field-Programmable Gate Array (FPGA)s. As a communication protocol to an external device for post-processing, USB was favored. USB is a widely used and well documented protocol.

2.3.1 Commercially available products.

A commercially available product is the MCHstreamer from miniDSP [24]. It already contains a microcontroller which performs preprocessing. The MCHstreamer provides connections for up to 16 MEMS microphones. There is no possibility to synchronize a MCHstreamer to an external clock source. This makes it impossible to cascade multiple MCHstreamer boards in order to increase the available number of microphones.

### 2.3.2 Field-Programmable Gate Array

A Field-Programmable Gate Array (FPGA) consists of logical blocks, which can be interconnected by programmable connections. This provides the maximum degree of freedom when programming the processor. However, the high degree of freedom can also become quite complex and time consuming very quickly.

Lattice Semiconductor Lattice provides a reference implementation for a PDM to PCM decimation for eight microphones [25]. Unfortunately, there is no reference implementation for a communication protocol like USB. A complete implementation of the USB stack is beyond the scope of this work and therefore not feasible.

33 opencores.org Opencores.org provides IP cores (reusable, already configured logic cells in a FPGA) in the typical hardware description languages Very High Speed Integrated Circuit Hardware Description Language (VHDL) or Verilog. The hardware description languages make the IP cores platform independent, they can be used with any compiler that can generate the bit file for the target. For the PDM to PCM decimation, a CIC filter core is available from [26]. However, the IP core was published in 2011 and last updated in 2014.
The website also provides an IP core for USB communications [27], which was last updated in 2019.

It is questionable whether the IP cores can be used directly without extensive changes in the source code. The long time since the release of the PDM IP core and the specific application for USB audio leads to the conclusion that it is too complex to use an FPGA as processing unit.

### 2.3.3 Microcontrollers

There is a large number of microcontrollers available on the market. Specific microcontrollers have been examined in more detail. The main criterion was on the availability of reference implementations for the data acquisition of MEMS microphones as well as a protocol for the communication with a host computer. A suitable reference implementation can serve as a good starting point and help to accelerate the development of the system.

ST Microelectronics ST Microelectronics provides a reference design for two microphones which utilizes the STM32F4 microcontroller [28]. The bit depth of the PCM output is fixed to 16 bit and at first glance, the generation of the sampling rate seems to be rather inaccurate (e.g. rounded sampling rates from 44.1 kHz to 44 kHz). An implementation of larger systems is not described and therefore, the feasibility is questionable.

Cypress Cypress provides a reference design for two microphones which utilizes their PSoC6 microcontroller [29]. In principle, the same problems occur here as in the implementation of ST microelectronics. There is a fixed bit depth of 16 bit and a rather limited sampling frequency generation. As with ST Microelectronics, it is not clear what issues might occur when implementing a larger number of microphones.

34

Analog Devices Analog Devices offers a large variety of Super Harvard Architecture Single-Chip Computer (SHARC) processors that can be used to process the digital microphone signal to a suitable signal for post-processing. An exemplary model is the ADSP-21489 [30]. This processor is used in the UMA-16 USB Mic Array from miniDSP [7]. Unfortunately, there is no corresponding reference implementation available and the miniDSP product uses proprietary code.

XMOS XMOS provides a reference design for seven microphones [31].There are reports of successful implementations of a larger number of microphones (e.g. in [32, 33]). The bit depth of the PCM signal can be set to either 16 bit or 24 bit and the generation of sample frequencies up to 48 kHz are supported.

### 2.3.4 Review results

A microcontroller from XMOS was selected as the processing unit. XMOS manufactures microcontrollers that are specialized in audio processing [34]. These microcontrollers are multicore controllers optimized for parallel processing. The designed system utilizes USB to transmit audio data to a host for post-processing. The selected device is the XUF216 [35] which provides an integrated USB Physical Layer (PHY) and a reference design for it.

## 2.4 xCore architecture

This section describes the most important features of the xCORE architecture which is utilized in all current XMOS products. Presented details are based on [36]. The xCORE architecture contains elements of a Real-Time Operating System (RTOS), e.g. a task scheduler, timers, channel communications and separate logical cores for real-time processing.
All xCore devices consist of one or more tiles which contain several logical cores and hardware resources like a reference clock. Each tile contains 64 KB of memory without cache as well as access to an I/O subsystem. The memory has no data bus contention since all peripherals are implemented with the I/O subsystem. There is no Direct Memory Access (DMA) for peripherals. The xCore architecture is illustrated in Fig. 2.18.

35

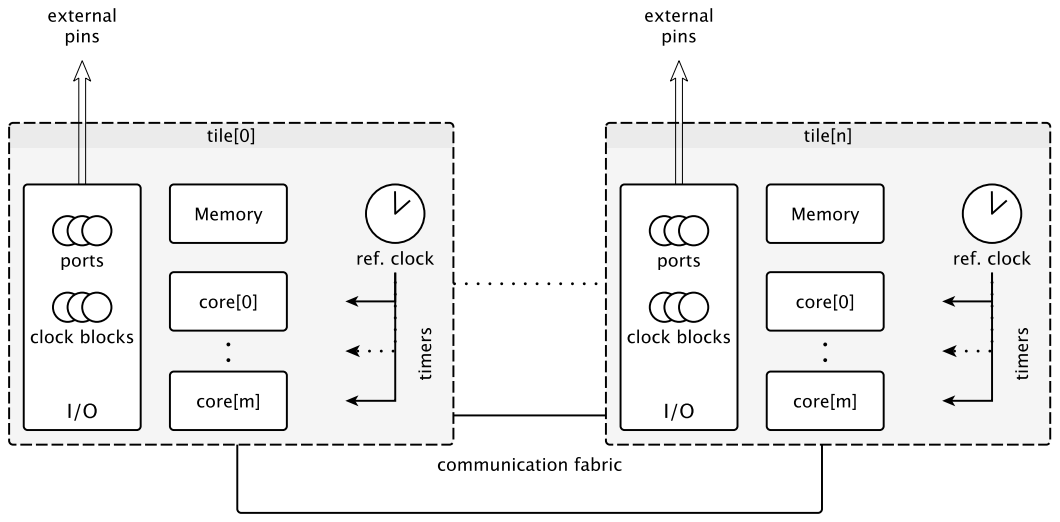
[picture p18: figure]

Figure 2.18: xCore hardware architecture, Figure from [36]

### 2.4.1 Cores

Cores are the units which execute code that result in tasks. Usually, multiple cores are combined in one tile. All cores in a tile run in parallel. Depending on the device configuration, cores can run in different speeds with a guaranteed minimum Million Instructions per Second (MIPS). Each task manages its own state and resources and can interact with other tasks by performing transactions.

### 2.4.2 Timers

Each tile comes with a reference clock running at a specified rate. The default rate is 100 MHz. Each reference clock is associated with a 32 bit wide counter. The counters on each tile are usually synchronized but not necessarily at the same value. With the 32 bit range of the counter it is possible to measure 2³² − 1 ticks, which is approximately 42 s at 100 MHz.

### 2.4.3 Communication

The communication between cores is provided by the communication fabric. This allows any core on any tile to access any other core on any other tile. Each software task can perform transactions with other tasks, whether it is on the same core (or

36

tile) or not.
Communication between tasks is realized with explicit transactions. All communication is point to point and can be either realized with an interface or a channel.

### Synchronous communication

Assume two tasks that run in parallel. Each task runs independently on its own data. At some point communication between the two tasks is necessary. The procedure is as follows:

1. Task 1 initiates a transaction with task 2
2. Task 1 waits until task 2 is ready to accept the transaction
3. Both tasks exchange relevant data
4. As soon as the data exchange is finished each task carries on

Since task 1 has to wait until task 2 responds to the transaction request, synchronous communication is called blocking communication.

### Asynchronous communication

In synchronous communication, the initiating task needs to wait for the requested task to answer the transaction request. This blocks further execution in the initiating task until it gets a response.
Sometimes it makes sense that the triggering task is not dependent on the requested task. Independence from the requested task is considered to be asynchronous and therefore can be called non-blocking communication. Asynchronous communication can by realized by the following approaches:
1. Notifications
This allows a task to raise a flag which indicates a wish to communicate with an other task. After the flag is raised, the initiating task can continue until the request is answered. This can be compared to a hardware interrupt.
2. Insert third task
A third task acts solely as a buffering task. It is inserted in the communication chain. Since the only job of this task is to buffer data it can be very responsive. The communication is realized with push and pull transactions to the buffer task. This can be compared to a shared memory First in, First out (FIFO) between two tasks.

37

### Interfaces

An interface provides a way of communication between cores. It defines the transaction type and what kind of data is exchanged between tasks. The interface connection is made of three parts:

- A definition of the connection via interface T
- A client type via client interface T
The client initiates the communication
- A server type via server interface T
The server responds to the communication request from the client and can send a notification to the client.

Only the client can initiate the communication. However, the server can notify the client by setting a flag. The notification is asynchronous and non-blocking. Notifications do not have arguments and their return value is always void. This means that the client has to initiate a communication after receiving a notification.

### Channels

Channels provide a primitive method of communication between tasks. Communication through a channel is blocking, but there is no prior definition of the transaction type.
A non-blocking channel is realized with a streaming channel. The data is exchanged over a streaming channel without synchronization between the tasks.

### 2.4.4 Event based reactions

It is possible for tasks to react to events. This is realized with a select() construct which pauses the task and waits for one or more events to occur. As soon as a defined event in the select statement occurs, the code in the relevant case is executed.
The select statement can contain multiple events but does only handle one event at a time. Select statements can be used as a substitute for interrupt routines.
The cases in a select statement are normally not prioritized. This means if two events happen at the exact same time it is undetermined which select case is executed. By adding the [[ordered]] attribute to the select construct, the cases are prioritized from the first (highest priority) to the last (least priority). Furthermore, it is possible to add a default case to a select statement. The default case is executed if no other statement is fulfilled.

38

### 2.4.5 Shared memory access

Tasks never share data by accessing common data types (e.g. global variables) which means that the usual synchronization methods (e.g. locks, mutex or semaphores) are not used. Common data is shared by making a request to an intermediate task that owns the data.

### 2.4.6 I/O

Each device has up to 64 physical digital outputs distributed across the tiles of the device. The pins are referred to as XnDpq, where n describes the tile number and pq the pin number.

### Ports

Pins are accessed over the hardware response ports. A port is responsible for driving output data on the pins or sampling input data. There are 29 ports available that have different port widths. The distribution is as follows: 16x 1 bit, 6x 4 bit, 4x 8 bit, 2x 16 bit and 1x 32 bit.
A port inputs or outputs all assigned bits at once. Therefore, ports should be used for I/O that work logically together. The pin to port mapping is fixed and can partially overlap. In general, overlapping ports should not be used together.

### Clock blocks

All ports are clocked and are therefore attached to a clock block in the device. This controls the read and write operations of the port.
Each port has a shift register which holds either output or input data, depending on the current port definition. At each clock tick, the port samples the input pins into the shift register or drives the output pins based on the contents of the shift register. A tile provides six clock blocks to which any port can connect. Every port can be set to either “divide” or “externally driven”.
In the “divide” mode, the port operates at an integer ratio of the reference clock (which is either 100 MHz or 500 MHz). In the “externally driven” mode, the port is synchronized to an external clock. All ports are connected to clock block 0 by default. This clock block provides the reference clock which always runs at 100 MHz.

39

### Writing and reading data to a port

The output of data on a port can be considered as a write operation. Inputting data on a port as a read operation. In both cases, a port declaration is necessary. For a write operation the appropriate data must be supplied, for a read operation the appropriate target.
A port can trigger an event when it is equal or not equal to a defined value. Selecting on conditional inputs is more power efficient than polling a port because it allows the processor to idle.

### Buffered ports

Using a buffered port can improve the performance of programs that perform input or output on clocked ports. A buffer can hold the data output by the processor until the next falling edge of the assigned clock. This allows the processor to execute other instructions during this time. A single thread can perform input and output operations on multiple ports in parallel when using buffered ports.

### 2.4.7 Parallelism

The xC programming language is an extension to the well-known C/C++ programming language. It provides an integration of parallelism and task management. Details on xC are presented in Sec. 2.4.9. It is up to the programmer to specify on which tile and core the tasks run in parallel. If no specifications are made, the compiler will automatically place the task on a free core.

### 2.4.8 Threads

In xC, three different tasks are distinguished from each other: normal, combinable and distributable. The differentiation between these three types help to optimize resource usage of the device.

### Normal tasks

Normal tasks run on a logical core and are independent from other tasks. They have a predictable running time and respond efficiently to external events. Unless otherwise specified, a task is considered “normal” by default.

40

### Combinable tasks

Combinable tasks are used to have several tasks running on the same logical core. The core swaps the tasks context based on cooperative multi-tasking. A combinable task has the following requirements:

- Void return type
- The last statement of the function must be a while(1) statement which contains a single select statement
- No channel communication between combined tasks. Interfaces are allowed.

### Distributable tasks

A task can contain a certain state and provides services to other tasks that do not need to react to external events. In this case, the task does not need an own core. It can share a core with the task(s) it communicates with. A distributable task has the following requirements

- It satisfies the requirements for a combinable task (while(1) loop and a single select statement)
- The cases in the select statement only respond to interface transactions

When a distributed task is connected to several other tasks, they cannot safely change their state at the same time. In this case, the compiler uses a lock to protect the state of the task.

### 2.4.9 Integrated Development Environment

XMOS provides an Integrated Development Environment (IDE) that contains fully standard compliant C/C++ compilation and their own xC extension. For the programming concepts in C and C++, please refer to [37, 38].
The xC extension provides task based parallelism and communication, accurate timing and access to the I/Os. All applications can be written in a mixture of xC and C/C++. It is possible to call a C/C++ function from xC and vice versa. The IDE used for this thesis is the xTimeComposer 14.4.1 on OS X 10.11.
It comes with an Eclipse[39] based Graphical User Interface (GUI) and provides [40]:
- Low Level Virtual Machine (LLVM) C, C++ and xC compilers

41

- xDEBUG: GDB multicore debugger
- xSIM: Cycle accurate simulator
- xSCOPE: In-circuit instrumentation and real-time logic analyzer
- XTA: Static timing analysis
- Platform support for Windows, Linux and OS X

### 2.4.9.1 References

The xC programming language introduces a data type called “reference” to indirectly refer to some data. The notation is not to be confused with pointers which are notated differently than in C/C++. The difference between pointers and references is the fact that pointers can be reassigned, while references cannot. Also, a reference must be assigned at initialization. A reference is indicated by an ampersand (&).

### 2.4.9.2 Pointers

Four different types of pointers are introduced which extend the pointer concept of C/C++: alias, restricted, movable and unsafe. A pointer is declared as follows:
1 poi n t e r −type ∗ poi n t e r−kind v a ri a bl e −name

If no kind is specified the compiler assumes the default kind which depends on the declaration location. Details are shown in Tab. 2.2 and are described in the following.

Declaration location Default pointer kind
Global variable | Restricted
Parameter | Restricted
Local variable | Alias
Function return | No default, must be explicitly declared

Table 2.2: Default kind for different pointer types

### Alias

Pointers are called alias pointers when two program elements refer to the same region of memory. Alias pointers have the following restrictions:

42

- It is not possible to pass alias pointers to different tasks that run in parallel.
- It is not possible to access an alias pointer indirectly (e.g. a pointer to an alias pointer)

It is possible to pass an alias pointer to a function that takes a restricted pointer as an argument if the passed pointer does not alias any of the other arguments.

### Restricted

A restricted pointer is a pointer that can not alias. The restricted pointer-kind allows to access the specific memory location only through that pointer. The non-alias property is checked by the xC compiler. A restricted pointer can be passed to a function which takes an alias pointer as an argument. Since restricted pointers can not be copied, they can not be used as return types for functions.

### Movable

A movable pointer is a pointer of which the ownership can be changed between parts of a program. This is used e.g. to

- transfer ownership to a global variable, which is used at a later time
- transfer ownership between tasks running in parallel

The movable kind is only possible with non-alias pointers since alias pointers could lead to race conditions or dangling pointers.
A moving pointer must point to the same region it was initialized with when it leaves the scope. It can be transferred between tasks that run in parallel via an interface function argument. Interfaces with pointer arguments can not be used across tiles due to the separate tile memory.

### Unsafe

Unsafe pointers are used for dynamic, aliasing data structures (e.g. linked lists). An unsafe pointer needs to be declared unsafe explicitly with the programmer ensuring memory safety. It comes with the following restrictions:

- Unsafe functions can only be called from unsafe regions.

43

- Within an unsafe region, an unsafe pointer can be cast to a safe pointer at the programmer’s liability
- If an unsafe pointer is written from one task and read from an other this results in undefined behavior

### 2.4.9.3 Nullable types

Some resources must always have a valid value (e.g. interfaces, chanends, ports or clocks). Therefore, the nullable qualifier is introduced. This qualifier indicates that the resources has currently no value. The nullable qualifier is marked by a question mark (?). It is useful for optional parameters in function calls.

### 2.4.9.4 Multiple return values

It is possible in xC to define functions with multiple return values. The return statement sets all values that need to be returned in brackets.

### 2.4.9.5 Memory safety

In C memory is allocated with the “malloc()” function. Access is only allowed to this allocated memory areas. Attempts to access memory outside the allocated area result in undefined behavior.
In xC an additional restriction is introduced: No task is allowed to access memory that is owned by an other task. Only the owning task can write to its memory area. It is possible though to change the ownership of a memory area.

### 2.4.9.6 Runtime exceptions and parallel usage checks

The xC compiler can detect out of bound errors during compile time. If the boundaries are unknown during the compilation (e.g. a function call with an array as a parameter), the compiler inserts a runtime check for safe memory operation.
If the operation is not safe an exception is raised and the program halts at the error where it can be debugged. For devices that go into final production the exception handler can make the device reboot if such an error occurs.

As already described, the memory safety of an xC program is ensured by the restriction that no other task can access the memory area than the owning task. This applies to parallel read/write operations, but not to parallel read-only operations.

44

## 2.5 USB overview

This section gives an overview of the general principles of the Universal Serial Bus (USB) as well as its audio specific part based on [41, 42, 43] and [32]. USB is a serial bus system that specifies hardware and a packet based communication protocol. It is used to transfer data between a host and at least one device in both directions. The term “host” describes the communication participant that can initiate the communication. The counterpart to the host is described by the term “device”, which can respond to communication requests but does not initiate communication.
The selected USB 2.0 standard differentiates between three speed grades: High-speed (operates at max. 480 Mbit/s), Full-speed (operates at max. 12 Mbit/s) and Low-speed (operates at max. 1.5 Mbit/s).
The system designed in this work operates at a sampling rate of 48 kHz with a bit depth of 24 bit. For a total number of 16 microphones per base board, the required bandwidth can be estimated to:
BWin, 24bit = 16 · 48 kHz · 24 bit ≈ 18.43 Mbit/s | (2.33)

The value of 18.43 Mbit/s exceeds the Low-speed grade and the Full-speed grade. Therefore, the High-speed grad is used.
The maximum bandwidth of 480 Mbit/s is limited by the data overhead that does not contribute to the payload. Examples are acknowledgements or the events that signal the start and end of a packet. A maximum effective bandwidth of 458.8 Mbit/s is specified for an isochronous transmission [41] (Details on the transmission mode are presented in Sec. 2.5.5). Assuming that the available bandwidth is distributed equally among all devices by a single USB controller, up to 24 base boards can be connected. Per base board, 16 microphones can be preprocessed which results in a total of 384 microphones. This estimate does not account for the write to memory speed, which is usually slower and further reduces bandwidth.

### 2.5.1 Endpoints

The USB provides a communication service between a host (running a specific software for the device) and the function on the device. Each communication flow from or to the device is terminated in an endpoint. Therefore endpoints can be seen as data sinks or data sources. The USB standard specifies that every device needs to provide at least one endpoint, called “endpoint 0”, which provides configuration information, the USB status and control access.

45

If more information needs to be transferred, additional endpoints can be implemented. In general, an endpoint is defined by the following properties:

- Bus access frequency/ latency requirement
- Bandwidth requirement
- Endpoint number
- Error handling behavior requirements
- Maximum packet size that the endpoint is capable to send or receive
- Transfer type of the endpoint
- Transfer direction.

The endpoint address is a unique combination of the device address, the endpoint number and the transfer direction. One endpoint is necessary per communication direction. This means that a bidirectional communication requires two endpoints, one that handles the data from the host to the device and the second in the reversed direction. Each interface can have up to eight endpoints for each communication direction.

### 2.5.2 Interfaces

An interface groups a number of endpoints together. Individual functions of the USB device can be accessed via interfaces. Examples of interfaces are:

- Input stream interface
- Output stream interface
- Audio control interface

### Alternate settings

Interfaces can have different modes of operation. The interface Identifier (ID) stays the same, while the alternate settings ID changes. The host knows the alternate settings ID. An example for an alternate setting is the option to use different sampling rates in the system.

### 2.5.3 Configuration

Different configurations can be used for a more flexible use of the device. A configuration is a collection of interfaces. Each configuration can define its own interfaces

46 or can have interfaces in common. The USB host chooses the configuration based on power consumption, available bandwidth and speed requirements of the device. The hierarchy between the configurations, interfaces and endpoints is illustrated in Fig. 2.19. The information about the device and the available configurations is provided in descriptors. More information on descriptors is given in Sec. 2.5.6.
There is always only one Device Descriptor but there can be multiple Configuration Descriptors, Interface Descriptors and Endpoint Descriptors.

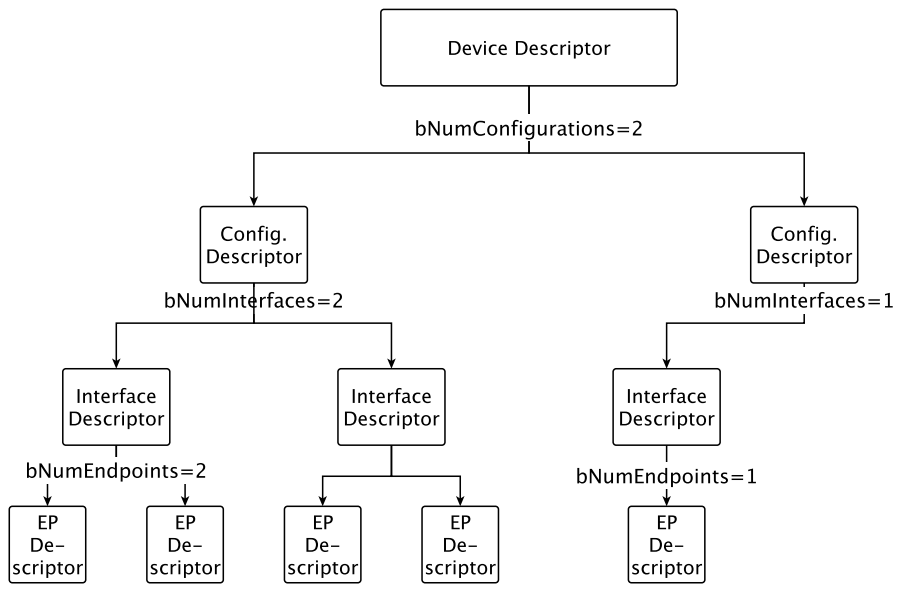
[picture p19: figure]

Figure 2.19: Descriptor hierarchy [41]

### 2.5.4 Device classes

The USB standard divides all devices into classes (e.g. human interface, printer or mass storage, etc.). All devices are required to provide information for their identification and generic configuration.
Each physical device can contain one or more device classes. A sound card could contain the Audio Device Class as well as the Human Interface Device (HID) class. If the device contains only one class, it is defined for the whole device in the Device Descriptor. If there is more than one class, each interface has its own class.
The relevant classes for this thesis are:

47

- Human Interface Device (HID)
Everything a human can interact with related to a computer.
- Audio Class
Specially for audio input and output, as well as all devices that control audio directly or indirectly (e.g. mixers, volume control).

### 2.5.5 Communication

The USB communication is a packet based. Data is transmitted in little endian, meaning the Least Significant Bit (LSB) is transmitted first. All transactions are initiated by the host, therefore the direction (e.g. input and output) refers to the point of view of the host. The host controls the transactions on the bus in order to avoid collisions.
The data is transmitted over a differential pair of wires. The transmission of the clock is encoded into the differential data with the Non-return-to-zero, inverted (NRZI) scheme, if necessary with adequate bit stuffing. To avoid confusion, the NRZI scheme is not part of the following descriptions.
Transmission errors can be detected by applying a Cyclic Redundancy Check (CRC) which calculates a checksum. This checksum can be used to identify erroneous data. In the best case transmission errors can be corrected with it.
As a further mechanism for minimizing transmission errors, bit stuffing is used. Here a zero is inserted after six consecutive ones to force a transition in the NRZI data stream. After seven bits at the latest, there is a transition that guarantees data and clock locks.

For the descriptions of data widths the binary and the hexadecimal notation are used in the following. The notation is identified in each case by a corresponding prefix: 0b<zeros or ones> for binary numbers and 0x<0 to F> for hexadecimal numbers. Decimal numbers are written without a prefix.

### 2.5.5.1 Packet types

Packets can be considered the smallest unit in the communication. The beginning and the end of each packet are signaled with specific events. This allows for a variable packet size, which is initially unknown to the receiver. Each packet is preceded by a SYNC field, allowing the receiver to synchronize their bit recovery clock. There are four different packet types with specific subtypes. A description of the packet types can be found in Tab. 2.3.

48

Type | Subtype | PID | Description
Token | SOF | 0xA5 | Start of frame marker
| SETUP | 0x2D | Initiates a control transfer
| OUT | 0xE1 | Initiates host to device data transfers
| IN | 0x69 | Initiates device to host data transfers
Data | DATA0 | 0xC3 | Data packet for toggled transfers, even
| DATA1 | 0x4B | Data packet for toggled transfers, odd
| DATA2 | 0x87 | Data packet for isochronous transactions
| MDATA | 0x0F | Data packet for split and isochronous transactions
Handshake | ACK | 0xD2 | Receiver accepts error free data packet
| NAK | 0x5A | Receiver can not accept data/ transmitter can not send
| STALL | 0x1E | Endpoint is halted/ control request is not supported
| NYET | 0x96 | Receiver buffer full, unable to receive more data
Special | PRE | 0x3C | (Token) Host issued preamble. Enables downstream
| | | traffic bus to Low-speed devices
| SPLIT | 0x78 | (Token) High-speed Split Transaction Token
| ERR | 0x3C | (Handshake) Split transaction Error Handshake (reuse
| | | of PRE value)
| PING | 0xB4 | (Token) High-speed flow control probe for a bulk/con-
| | | trol endpoint

Table 2.3: USB packet types

Each packet can be identified by its Packet Identifier (PID) field. This field is eight bits long and can be divided into two portions: the normal portion and the inverted portion. The PID field is depicted in Fig. 2.20.

0 | 1 | 2 | 3 | 4 | 5 | 6 | 7
PID0 | PID1 | PID2 | PID3
PID0 | PID1 | PID2 | PID3

Figure 2.20: PID field, Figure from [41]

### Token Packets

The specification distinguishes between Start of Frame (SOF) packets and all other token packets listed in Tab. 2.3. The structure of the IN, OUT and SETUP packets is identical and is shown in Fig. 2.22.
Token packets have a five bit Cyclic Redundancy Check (CRC) that covers the address and endpoint field in case of a IN, OUT and SETUP packet. The CRC of

49 the SOF packet covers the Frame Number field. The PID field has its own check field.

Start of Frame (SOF) This packet is sent at each start of a microframe. In lower speed grades, a SOF is sent every 1 ms. In High-speed mode, a microframe starts each 125 µs ± 0.0625 µs. The receiver generates no Acknowledgement (ACK) packet for a SOF packet. Therefore, the delivery of a SOF packet can not be guaranteed. The frame number is calculated in a binary manner. It is increased every millisecond to be compliant to the lower speed grades. Due to the binary calculation of the counter, an overflow sets the frame number back to zero. For the given time span of 1 ms this results in the same frame number for eight consecutive SOF packets. The SOF structure is depicted in Fig. 2.21.

0 | 7 8 | 18 19 | 23
PID:0xA5 | Frame No | CRC5

Figure 2.21: Start of Frame (SOF) packet, Figure from [41]

SETUP A control transfer is initiated by the setup packet. More details on the transfer types are presented in Sec. 2.5.5.2. The address and endpoint field identify the endpoint that will receive the subsequent data packet. The structure is depicted in Fig. 2.22.

OUT/IN A data transfer is initiated by the OUT/IN packets either from or to the host. This packet is followed by a data packet from either the host or the device. The address and endpoint field identify the endpoint that either receives (OUT) or sends (IN) the data packet. The structure is depicted in Fig. 2.22.

0 | 7 8 | 14 15 | 18 19 | 23
PID | Address | Endpoint
No. | CRC5

Figure 2.22: IN, OUT, SETUP packet, Figure from [41]

50

### DATA Packets

After the communication is initiated by either a SETUP, OUT or IN packet, the DATA packet is sent. The content of the packet depends on the transfer type and application type. The 16 bit CRC covers the data field. The structure of a DATA packet is depicted in Fig. 2.23.

PID | Data | CRC16
8 bit | 0 to 8192 bit | 16 bit

Figure 2.23: Data packet structure, Figure from [41]

There are four different data packets PIDs: DATA0, DATA1, DATA2 and MDATA. DATA0 and DATA1 PIDs are used for toggled data transmission. In a normal transmission, each packet needs to be acknowledged by the receiver. After the sender receives the acknowledgement, the next packet is sent. If an acknowledgement is lost, the sender retransmits the previous packet. This avoids transmission errors. The behavior is shown in Fig. 2.24.

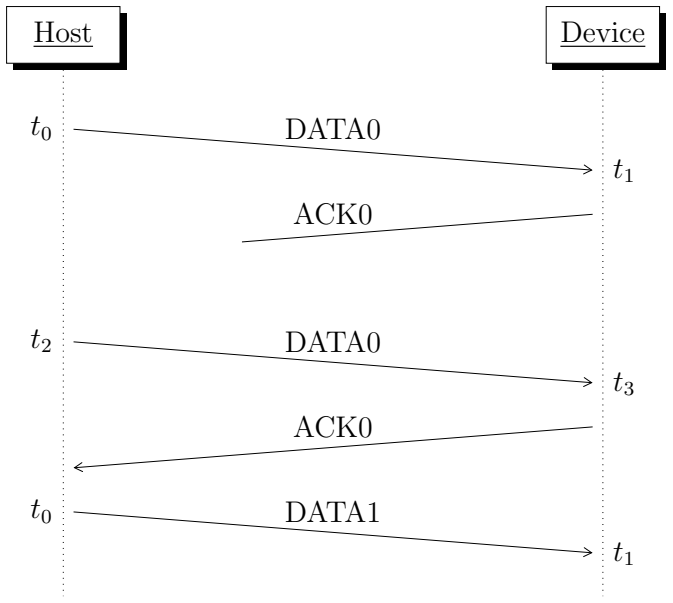
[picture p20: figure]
Host; Device; DATA0; ACK0; DATA1

Figure 2.24: Retransmission after lost ACK

Up to three isochronous or interrupt transfers per microframe are possible for a

51

High-speed transmission (Sec. 2.5.5.2 describes the transfer types). The PID order is defined by the size of the data and the data direction. If the data size is larger than 1024 byte, the transfer is split into multiple transactions. The exact data size is class or vendor specific. The data sizes quoted in this document are suggestions from the specification. Since this thesis utilizes the isochronous transfer type, only the PID ordering for this mode is shown. For isochronous IN transmissions, the PIDs are:

- 1 transaction (< 1024 byte): DATA0
- 2 transactions (513 to 1024 byte): DATA1, DATA0
- 3 transactions (683 to 1024 byte): DATA2, DATA1, DATA0

For isochronous OUT transmissions, the PID sequence is:

- 1 transaction (< 1024 byte): DATA0
- 2 transactions (513 to 1024 byte): MDATA, DATA0
- 3 transactions (683 to 1024 byte): MDATA, MDATA, DATA2

If an erroneous OUT transaction is detected, all data transferred during that microframe is discarded. The identical PIDs for three transactions are intended. It is up to the vendor to implement a method to detect which MDATA packet has been lost.

### Handshake Packets

Handshake packets are used for feedback on the previous transmission. A handshake packet can be used to signal successful data reception, command acceptance/rejection, flow control and holding conditions. The packet consists only of the PID field and is shown in Fig. 2.25.

0 | 7
PID

Figure 2.25: Handshake packet, Figure from [41]

ACK Indicates that the previous packet was received correctly without bit stuffing or CRC errors. An ACK packet is transmitted by the host for all IN transactions and by the device for OUT, SETUP and PING transactions.

52

NAK Indicates a communication error with the previously sent packet. For an OUT packet this means that the device was unable to receive the packet, for an IN packet that the device has no data to transmit. A NAK is only issued by a device and never by the host.

STALL Reports that the device is currently unable to receive or send packets. Exception: STALL after a SETUP packet indicates that the device does not support the host request.

NYET Used for bulk out transfers. Indicates that the buffer of the device is full and it can not receive any more packets. The host has to poll the device with ping packets.

### Special packets

PING Packets A PING packet is used to poll whether the device has enough space in the internal buffer to receive bulk messages. The device answers with ACK if it can receive more data or with NAK if not. The structure of a PING packet is identical to the Token structure which is depicted in Fig. 2.22.

PRE, SPLIT and ERR Packets These packets are used to enable lower speed communication on a higher speed bus over a hub. They are not relevant for this work and are therefore not explained in detail here.

### 2.5.5.2 Transfer types

USB 2.0 provides four different transfer types that are optimized for specific purposes: Control Transfer, Isochronous Transfer, Interrupt Transfer and Bulk Transfer. A transfer type is determined by the following characteristics:

- Data format imposed by the USB
- Direction of communication flow
- Packet size constraints
- Bus access constraints
- Latency constraints
- Required data sequences
- Error handling

53

### Control Transfer

Control Transfers can be described as bursty, non-periodic communications that are initiated by the host. This transfer type is usually used for requesting USB descriptors, the device configuration or for status operations. It is the first transfer mode when a new device is added to the bus. The stages of a Control Transfer are:

- Setup stage
The host initiates control transfer with a SETUP packet, followed by a DATA0 packet containing the request. The device acknowledges the packet. The sequence is shown in Fig. 2.26.

Figure 2.26: Control Transfer Setup stage, Figure from [41]

- Data stage
Used for control transfers or requests where data must be transferred to or from the device. In the previous stage, the size of the data to be transferred is specified. Depending on the size of the data and the maximum packet size defined by the device, this stage may consist of one or more IN or OUT transmissions. The sequence is shown in Fig. 2.27.

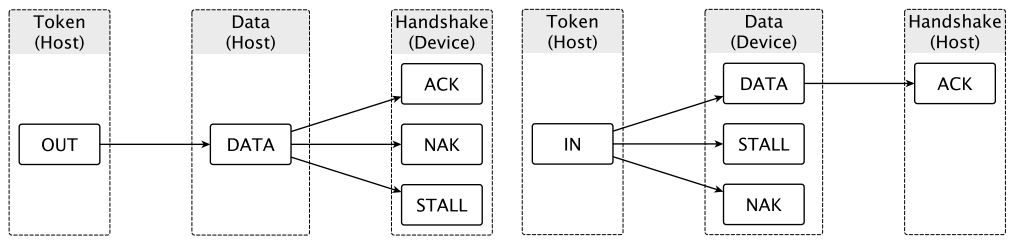
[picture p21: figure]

(a) OUT | (b) IN

Figure 2.27: Control Transfer Data stage, Figure from [41]

54

- Status stage
The success or failure of whole Control Transfer is reported in this stage. It starts with an IN/OUT packet which is opposite to the direction from the data stage. The successful reception of the data is acknowledged by a DATA0 packet of zero length. The sequence is shown in Fig. 2.28.

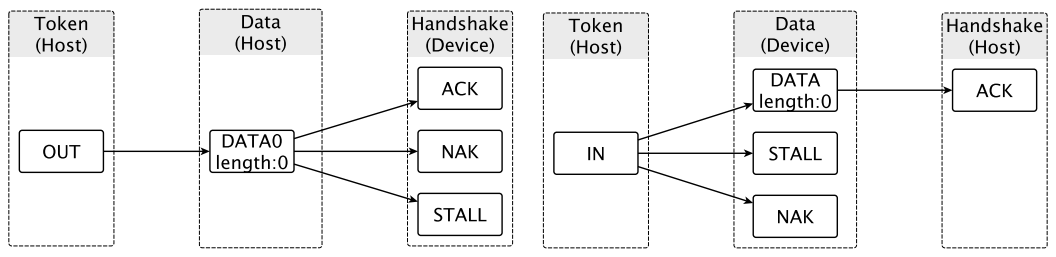
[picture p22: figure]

(a) OUT | (b) IN

Figure 2.28: Control Transfer Status stage, Figure from [41]

### Isochronous Transfer

Isochronous Transfers are used for data that is streamed continuously. With this transfer type, a time slot is reserved in each frame, which guarantees a certain bandwidth. The error handling scheme for the Isochronous Transfer does not allow for retransmission of faulty or lost packets. This transfer mode should be used if data loss can be tolerated. The transmission sequence is shown in Fig. 2.29.
The required bandwidth is set in the Endpoint Descriptor. If there is not enough bandwidth left on the bus, the device is rejected at startup. If an Alternate Setting is available (for example a data reduced transmission) this fallback is used.
The data rate can be synchronized between the host and the device. Synchronization can be achieved using the following approaches:
- No synchronization
Only used if there is no real-time application and the data rate is not of importance
- Synchronous
The device synchronizes with the host by locking to the SOF packets from the host.

55

- Asynchronous
The sender adjusts the transmission rate to prevent receiving buffer over- or underflow. Requires a feedback endpoint on the receiver side which reports on the fill level of the receiving buffer.
- Adaptive
The device is able to synchronize itself to the data rate required by the host.
(a) OUT | (b) IN

Figure 2.29: Isochronous transfer, Figure from [41]

### Interrupt Transfer

Interrupt Transfers are used to receive interrupts from the device. The term interrupt should not be confused with the conventional definition of an interrupt. The host has to poll the device periodically in order to receive the interrupts. With interrupt transfers there is a guaranteed latency. If a checksum error occurs the transfer is retried in the next polling period. The polling period is defined in USB frames. The transmission scheme is shown in Fig. 2.30.

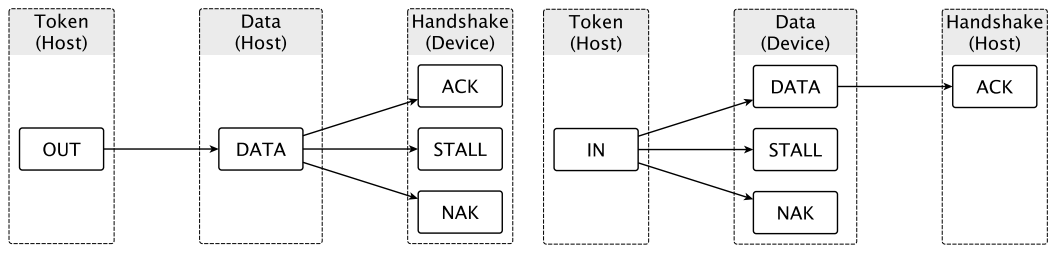
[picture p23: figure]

(a) OUT | (b) IN

Figure 2.30: Interrupt transfer, Figure from [41]

56

### Bulk Transfer

A Bulk Transfer is used for large data transfers that are not time-critical but often occur in bursts. Data is transferred if there are time slots available after the Isochronous and the Interrupt Transfers. Therefore, this transmission mode neither guarantees a certain latency or bandwidth. Error detection and retransmission mechanisms are provided. The transmission sequence is shown in Fig. 2.31.

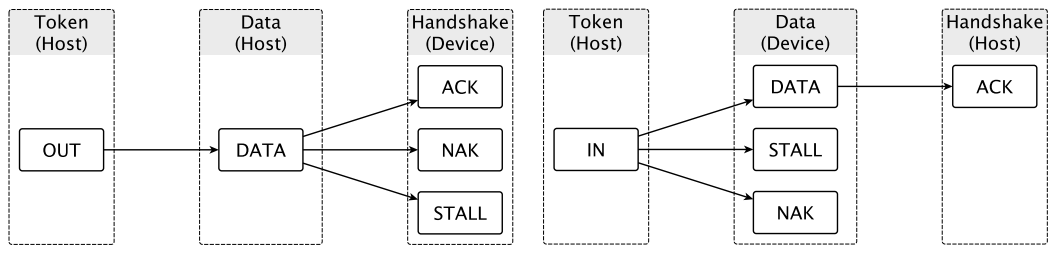
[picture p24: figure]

(a) OUT | (b) IN

Figure 2.31: Bulk transfer, Figure from [41]

### 2.5.5.3 Request types

Requests are used to retrieve information about the device, configuring the device or checking the status of the device. Every device has to implement standard and class specific requests. Due to identical naming of the packets, requests are not to be confused with transfers.

### Setup Packet

A request starts with the setup stage and is followed by a DATA0 packet, which contains a 8 byte setup packet. The structure is described in Tab. 2.4. The bmRequestType field depends on the transfer direction, the type and the recipient. The values of the wValue, wIndex and wLength fields depend on the request. The layout of the field is shown in Fig. 2.32. In case the request needs data to be transferred, a Data Stage follows.

57

Offset | Field name | Bytes | Description
0 | bmRequestType | 1 | Direction, Type and Recipient
1 | bRequest | 1 | ID of the request
2 | wValue | 2 | Request dependent value
4 | wIndex | 2 | Request dependent value
6 | wLength | 2 | Request dependent value

Table 2.4: Setup packet details

The bmRequestType field is coded as follows:

76540
Recipient | Type | Trans dir

Figure 2.32: bmRequestType field for a SETUP packet, Figure from [41]

The subfields define the following:

- Recipient, 5 bit
0: Device
1: Interface
2: Endpoint
3: Other
- Type, 2 bit
0: Standard
1: Class
2: Vendor
3: Reserved
- Transfer direction, 1 bit 0: OUT
1: IN

### Standard Request

All standard requests of the USB 2.0 protocol are shown in Tab. 2.5. The getter and setter requests are also depending on the direction and recipient bits in the bmRequestType field and therefore listed separately.

58

bmRequest | Recipient | wValue | wIndex | Data
Get status | Device | - | - | Status
| Interface | - | Interface | Status
| Endpoint | - | Endpoint | Status
Clear/Set Feature | Device | Feature | - | -
| Interface | Feature | Interface | -
| Endpoint | Feature | Endpoint | -
Set Address | Device | Address | - | -
Get/Set Descriptor | Device | Type or Index | - / Language | Descriptor
Get/Set Configuration | Device | - | - | Config. Value
Get/Set Interface | Interface | Alternate Setting | Interface | -
SYNCH FRAME | Endpoint | - | Endpoint | Frame No.

Table 2.5: Standard Requests for USB 2.0

- Get status request
The status of the device, interface or endpoint are retrieved with this request. Returns 2 byte, each bit represents a boolean status. The USB 2.0 standard defines the following recipients with the following return information: – Device
Bit 0: Self Powered
Bit 1: Remote Wakeup

– Endpoint
Bit 0: Halted
Bit 1: Stalled

– Interface
No return information specified for interfaces.
- Clear/Set Feature
Used to set or clear following features as a true/false value:

– Device
Set the remote wakeup feature
Set the device into test mode

– Endpoint
Halt an endpoint

– Interface
The interface does not provide any features
- Set Address
Sets address of the USB device after plugging in.
- Get/Set Descriptor
Used in the initiation phase to request the descriptors of the device. In normal

59 operation, set functions are usually not used.

- Get/Set Configuration
With the set function, a Configuration Descriptor is selected as the current configuration. The number of the currently active Configuration Descriptor is returned by the get function.
- Get/Set Interface
Toggles between different alternative settings of a specific interface.
- SYNCH FRAME
Used for isochronous endpoints with varying frame sizes. The variation of the frames is performed in patterns (e.g. 2, 3, 3). The frame number of the beginning of this pattern is returned by this request.

### 2.5.5.4 Enumeration process

Communication begins when the host detects the connection of a device by measuring the voltage change caused by the pull-up resistors on the data lines of the device. A reset command is then sent by the host. This temporarily sets the device address to zero, which is why the host can only process one device at a time.
After the reset, the device is addressable and communication can start. At this point it acts as a basic USB device with no specific function. It can only answer to the standard control requests from and to endpoint 0.
In the next step, the host requests the Device Descriptor of the device to determine the maximum packet length (Descriptors are explained in Sec. 2.5.6). The packet length is defined by the receive buffer of the device. After this, the host resets the device again and then sends a “set address request” which assigns an unused address to the device.
As soon as the unique address is assigned to the newly connected device, the host can start the described procedure with any other newly connected device.
Once the device is assigned a unique address, the actual initialization and configuration of the device begins. The host requests all descriptors: the Device Descriptor, the Configuration Descriptors and all String Descriptors. In a last step, the host selects a configuration and sends the configuration request. The described process is called enumeration process.

60

### 2.5.6 Descriptor types

Descriptors are requested from the host as soon as a device is assigned a unique address. They are composed of a hierarchical system of sub descriptors. The hierarchy of the descriptors is shown in Fig. 2.19. In addition, they contain a list of strings that can be referenced in other descriptors. Each descriptor starts with the same two fields: bLength and bDescriptorType. The bLength field defines the length of the whole descriptor in bytes. The bDescriptorType field defines the descriptor type. The subsequent fields are descriptor dependent. The root element of the USB descriptor hierarchy is the Device Descriptor.

### 2.5.6.1 Device Descriptor

The device information is contained in the Device Descriptor, for example USB version, manufacturer, serial number, etc. The structure of the descriptor is shown in Tab. 2.6, the descriptor fields are explained in the following.

Offset Field name | Bytes Description
0 | bLength | 1 | Descriptor length: 18 bytes
1 | bDescription Type | 1 | 0x01 (Device Descriptor ID)
2 | bcdUSB | 2 | Version
4 | bDeviceClass | 1 | Device Class Code
5 | bDeviceSubClass | 1 | Subclass Code
6 | bDeviceProtocol | 1 | Protocol Code
7 | bMaxPacketSize | 1 | Max Packet Size of Endpoint 0
8 | idVendor | 2 | Vendor ID (USB Org)
10 | idProduct | 2 | Product ID
12 | bcdDevice | 2 | Device Release Number
14 | iManufacturer | 1 | Index of String Descriptor
15 | iProduct | 1 | Index of String Descriptor
16 | iSerialNumber | 1 | Index of String Descriptor
17 | bNumConfigurations 1 | Number of available configurations

Table 2.6: Format of the Device Descriptor

- bLength
Descriptor length. Always 18 byte for USB 2.0

61

- bDescriptionType
Set to 0x01. Identifies the descriptor type as the Device Descriptor.
- bcdUSB
USB version in the format 0xJJMN. J: major, M: minor, N: sub minor version.
- bDeviceClass
Specifies the class for the whole device

– 0x00: Each interface specifies its own class code

– 0xFF: Vendor specified class code

– 0xFE: The interface defines the class and an Interface Association Descriptor is present

- bDeviceSubClass & bDeviceProtocol
The correct driver for the device is selected here. Is normally only defined at the interface level.
- bMaxPacketSize
Defines the maximum packet size in accordance with the buffer size of endpoint 0.
- iVendor & iProduct
Uniquely identify the product. Vendor IDs are assigned by the USB Implementers Forum
- bcdDevice
Device version number. Is in the same format as bcdUSB.
- iManufacturer, iProduct & iSerialNumber
Index of the string descriptor for the human readable strings to describe the device
- bNumConfigurations
Number of the available configurations of the device. This is used to request all Configuration Descriptors

62

### 2.5.6.2 String Descriptor

String Descriptors provide human-readable strings for the functions provided by the device. String Descriptors are optional. If a device does not support any String Descriptors, all String Descriptors must be set to zero.
All strings used in a descriptor are referenced by an ID and stored in a string descriptor. Using the combination of String Descriptor ID and Language ID, the host can request the desired string descriptors with a “String Descriptor request”. The device then returns the corresponding string descriptor as shown in Tab. 2.8.
It is possible to provide the strings in different languages. Available language IDs can be found in the special string descriptor with ID 0. Its structure is shown in Tab. 2.7. The fields of the String Descriptor are described below.
Offset | Field name | Bytes Description
0 | bLength | 1 | String descriptor length
1 | bDescriptionType 1 | 0x03, String Descriptor ID
2 | wLANGID[0] | 2 | LANGID Code 0
2 + 2 · n wLANGID[n] | 2 | LANGID Code n

Table 2.7: Available Languages ID String Descriptor, addressed with ID 0

Offset Field name | Bytes Description
0 | bLength | 1 | String descriptor length
1 | bDescriptionType 1 | 0x03, String Descriptor ID
2 | bString | N | String encoded in Unicode

Table 2.8: String Descriptor, addressed from ID 1 and above

| • bLength
Descriptor length. Depends on the string length or number of languages
| • bDescriptionType
Set to 0x03. Identifies the String Descriptor type.
| • bString in Tab. 2.8
The string encoded in Unicode. The size depends on the length of the string.
| • wLANG[n] in Tab 2.7
Language ID. E.g. English (United States): 0x0409 in little endian.
| | | 63
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

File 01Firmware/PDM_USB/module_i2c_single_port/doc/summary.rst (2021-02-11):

I2C interface summary
=====================

I2C is the Philips 2 wire interface, used to configure many digital chips.
I2C software has the following options:

* Whether we are a *master* or a *slave*. Devices that are configured are
  slaves, the master configures other devices. 

* The speed supported. Normal speeds are 100 Kbps and 400 Kbps. 

* Whether there is a single I2C bus or multiple I2C buses.

* Whether there is a single master or multiple masters.

* Whether clock stretching is supported.

module_i2c_single_port
----------------------

This module supports single master, at 100 or 400, 1000 kbps without clock
stretching, where both SCL and SDA are shared on a single port (4, 8, 16,
or 32 bits wide).

.. table::
 :class: vertical-borders horizontal-borders

 +---------------------------+-----------------------+------------------------+
 | Functionality provided    | Resources required    | Status                 | 
 |                           +-----------+-----------+                        |
 |                           | Ports     | Memory    |                        |
 +---------------------------+-----------+-----------+------------------------+
 | Single master             | 1         | 360 bytes | Implemented            |
 +---------------------------+-----------+-----------+------------------------+

The interface comprises four functions, init and reg_write
that are called when required. No separate logical core is required.

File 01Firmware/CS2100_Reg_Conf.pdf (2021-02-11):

Device Address | 0x4e
Address | 0x01 | Device ID
Bit | 7 | 6 | 5 | 4 | 3 | 2 | 1 | 10
Description | Device ID | | | | | Revision
Default Val | 0 | 0 | 0 | 0 | 0 X | | X | X
INT CLK | r | r | r | r | r | r | r | r
EXT CLK | r | r | r | r | r | r | r | r
Address | 0x02 | Device Ctrl
Bit | 7 | 6 | 5 | 4 | 3 | 2 | 1 | 0
Description | Unlock | Reserved | | | | | AuxOutDis | ClkOutDis
Default Val | X | 0 | 0 | 0 | 0 | 0 | 0 | 0
INT CLK | 0 | 0 | 0 | 0 | 0 | 0 | 0 | 0
EXT CLK | 0 | 0 | 0 | 0 | 0 | 0 | 0 | 0
Address | 0x03 | Device Config 1
Bit | 7 | 6 | 5 | 4 | 3 | 2 | 1 | 0
Description | RmodSel | | | Reserved | Reserved | AuxOutSrc | | EnDevCfg1
Default Val | 0 | 0 | 0 | 0 | 0 | 0 | 0 | 0
INT CLK | 0 | 0 | 0 | 0 | 0 | 1 | 0 | 1
EXT CLK | 0 | 0 | 0 | 0 | 0 | 1 | 0 | 1
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

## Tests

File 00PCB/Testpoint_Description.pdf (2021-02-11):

Sheet1

Name | Description | Output | Name | Description | Output
T0S1 | Spare Output for Tile0 | | TP44 | MC_02_DATA_P | PDM Data
T0S2 | Spare Output for Tile0 | TP45 | MC_01_02_CLK_IN_P 3.072MHz
T0S3 | Spare Output for Tile0 | TP46 | MC_01_02_CLK_IN_N 3.072MHz
T0S4 | Spare Output for Tile0 | | TP47 | MC_01_DATA_P | PDM Data
T1S1 | Spare Output for Tile1 | | TP48 | MC_01_DATA_N | PDM Data
T1S2 | Spare Output for Tile1
T1S3 | Spare Output for Tile1 | | TP49 | AUX OUT CS2100
T1S4 | Spare Output for Tile1 | | TP50 | AUX OUT CS2100
| | | TP65 | 25M576 Crystal out | 24.576MHz
TP01 | MC_16_DATA_N | PDM Data | TP66 | 1V Output | 1V
TP02 | MC_16_DATA_P | PDM Data | TP67 | 3V3 Output | 3.3V
TP03 | MC_15_16_CLK_IN_P 3.072MHz | TP68 | USB_VBUS | 5V
TP04 | MC_15_16_CLK_IN_N 3.072MHz | TP69 | USB_D_P | USB Data
TP05 | MC_15_DATA_P | PDM Data | TP70 | USB_D_N | USB Data
TP06 | MC_15_DATA_N | PDM Data | TP71 | PG_3V3 | 3.3V
TP07 | MC_14_DATA_N | PDM Data | TP72 | POR | 3.3V
TP08 | MC_14_DATA_P | PDM Data | TP73 | RST_N | 3.3V
TP09 | MC_13_14_CLK_IN_P 3.072MHz | TP74 | WCLK_IN_BUF | 48kHz
TP10 | MC_13_14_CLK_IN_N 3.072MHz | TP76 | MCLK_INTERN | 12.288MHz
TP11 | MC_13_DATA_P | PDM Data | TP77 | I2C_SDA | I2C Data
TP12 | MC_13_DATA_N | PDM Data | TP78 | I2C_SCL | I2C Clock
TP13 | MC_12_DATA_N | PDM Data | TP79 | REF_IN0_P | 3.072MHz
TP14 | MC_12_DATA_P | PDM Data | TP81 | MCLK_EXTERN | 12.288MHz
TP15 | MC_11_12_CLK_IN_P 3.072MHz | TP82 | MIC_CLK | 3.072MHz
TP16 | MC_11_12_CLK_IN_N 3.072MHz | TP83 | CLK_SRC_SEL | 0V/3.3V
TP17 | MC_11_DATA_P | PDM Data | TP100 | CLK_24M | 24MHz
TP18 | MC_11_DATA_N | PDM Data | TP101 | GND | GND
TP19 | MC_10_DATA_N | PDM Data
TP20 | MC_10_DATA_P | PDM Data | 5V | 5V | 5V
TP21 | MC_09_10_CLK_IN_P 3.072MHz | AG1 | Analog Ground | GND
TP22 | MC_09_10_CLK_IN_N 3.072MHz
TP23 | MC_09_DATA_P | PDM Data
TP24 | MC_09_DATA_N | PDM Data
TP25 | MC_08_DATA_P | PDM Data
TP26 | MC_08_DATA_N | PDM Data
TP27 | MC_07_08_CLK_IN_P 3.072MHz
TP28 | MC_07_08_CLK_IN_N 3.072MHz
TP29 | MC_07_DATA_P | PDM Data
TP30 | MC_07_DATA_N | PDM Data
TP31 | MC_06_DATA_N | PDM Data
TP32 | MC_06_DATA_P | PDM Data
TP33 | MC_05_06_CLK_IN_P 3.072MHz
TP34 | MC_05_06_CLK_IN_N 3.072MHz
TP35 | MC_04_DATA_P | PDM Data
TP36 | MC_05_DATA_N | PDM Data
TP37 | MC_04_DATA_N | PDM Data
TP38 | MC_04_DATA_P | PDM Data
TP39 | MC_03_04_CLK_IN_P 3.072MHz
TP40 | MC_03_04_CLK_IN_N 3.072MHz
TP41 | MC_03_DATA_P | PDM Data
TP42 | MC_03_DATA_N | PDM Data
TP43 | MC_02_DATA_N | PDM Data

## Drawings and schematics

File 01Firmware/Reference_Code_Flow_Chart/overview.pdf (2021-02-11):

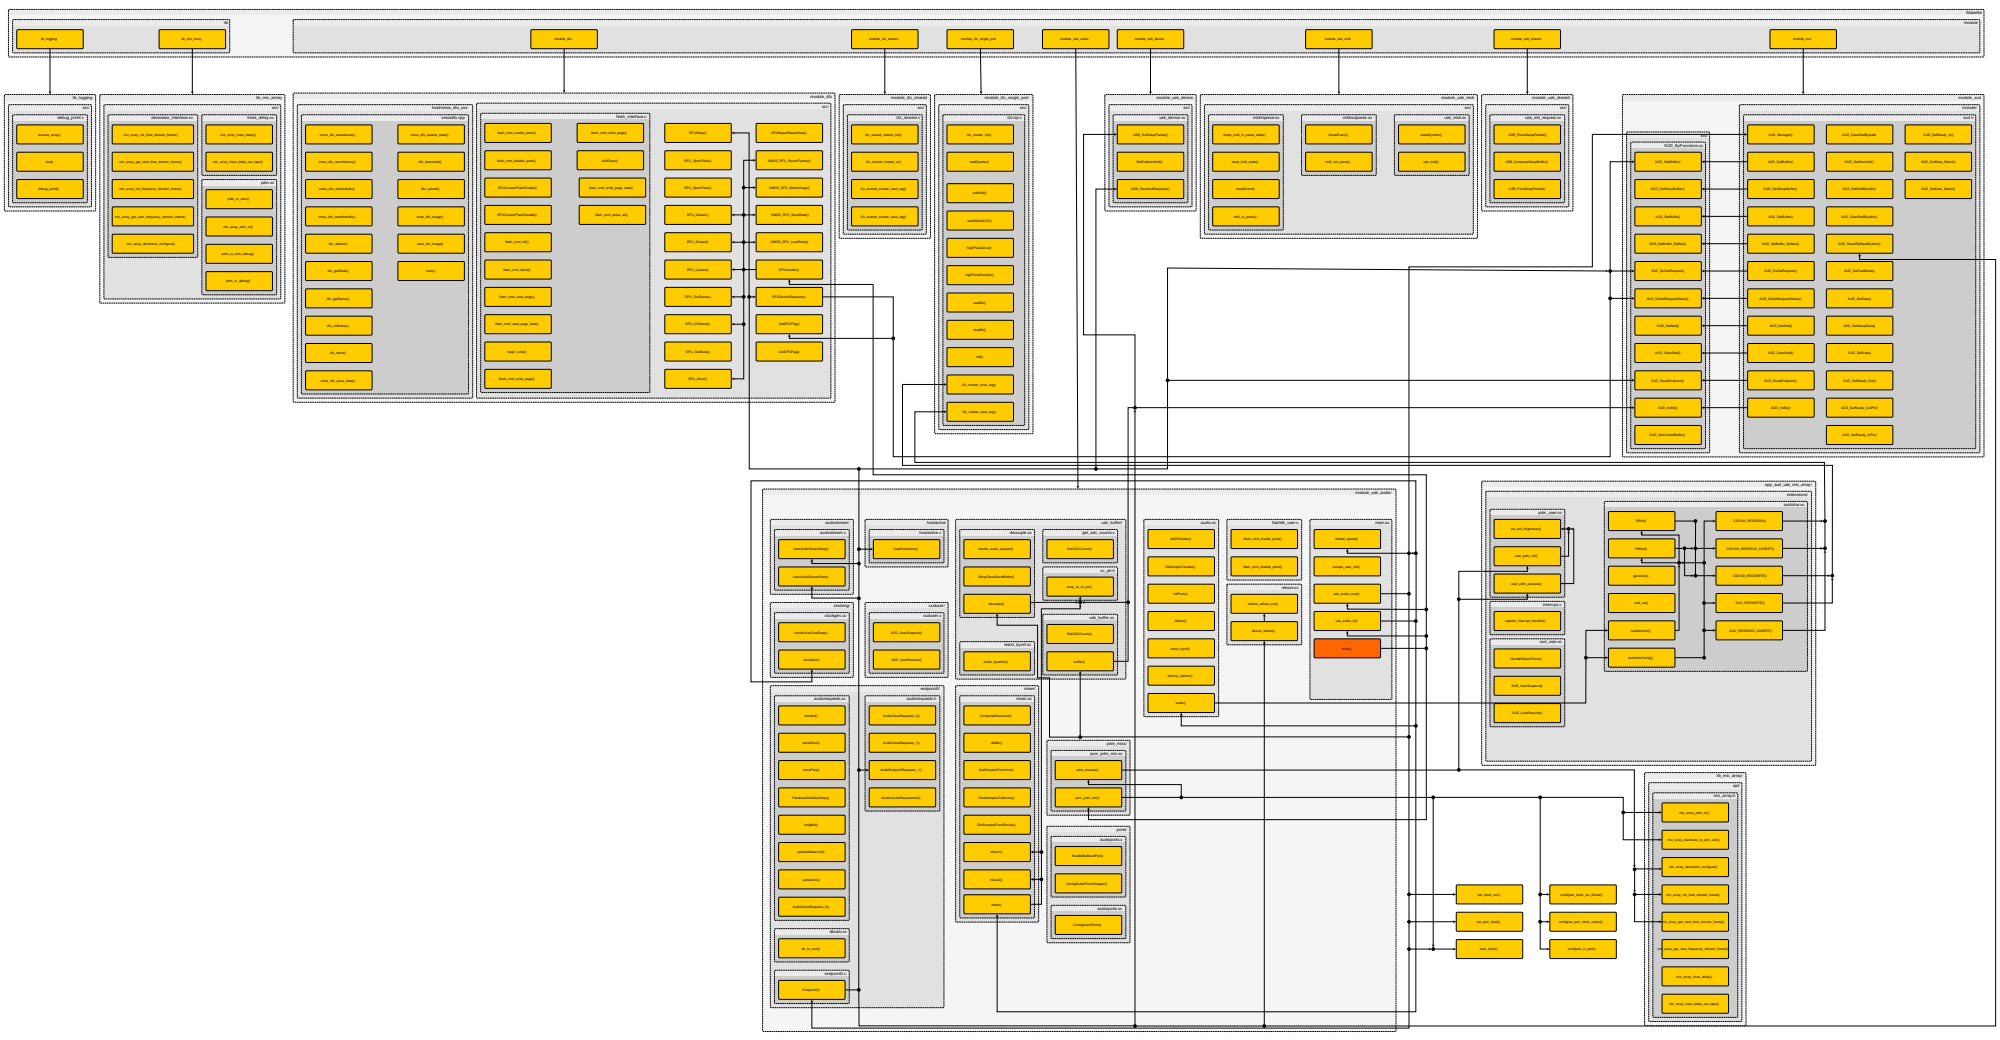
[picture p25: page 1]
app_aud_usb_mic_array/; extensions/; pdm_user.xc; user_pdm_process(); set_led_brightness(); user_pdm_init(); xud_user.xc; HandleRebootTimer(); XUD_UserSuspend(); XUD_UserResume(); interrupt.c; register_interrupt_handler(); audiohw.xc; PllInit(); PllMult(); genclock(); wait_us(); AudioHwInit(); AudioHwConfig(); CS2100_REGREAD(); CS2100_REGREAD_ASSERT(); CS2100_REGWRITE(); DAC_REGWRITE(); DAC_REGREAD_ASSERT(); module_usb_audio/; pdm_mics/; pcm_pdm_mic.xc; pdm_process(); pcm_pdm_mic(); audio.xc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

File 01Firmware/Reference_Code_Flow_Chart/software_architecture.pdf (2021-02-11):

### tile[0]

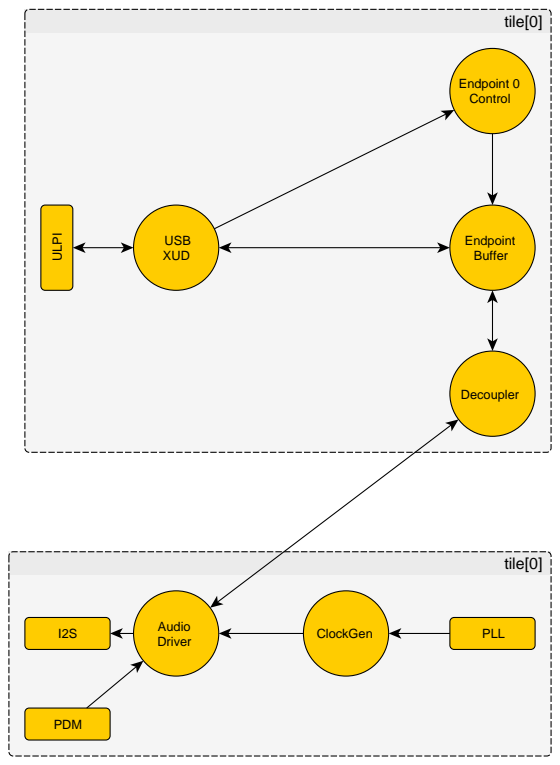
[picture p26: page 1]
USB XUD; Endpoint 0 Control; Endpoint Buffer; Decoupler; ULPI; tile[0]; Audio; Driver I2S; ClockGen; PLL; PDM

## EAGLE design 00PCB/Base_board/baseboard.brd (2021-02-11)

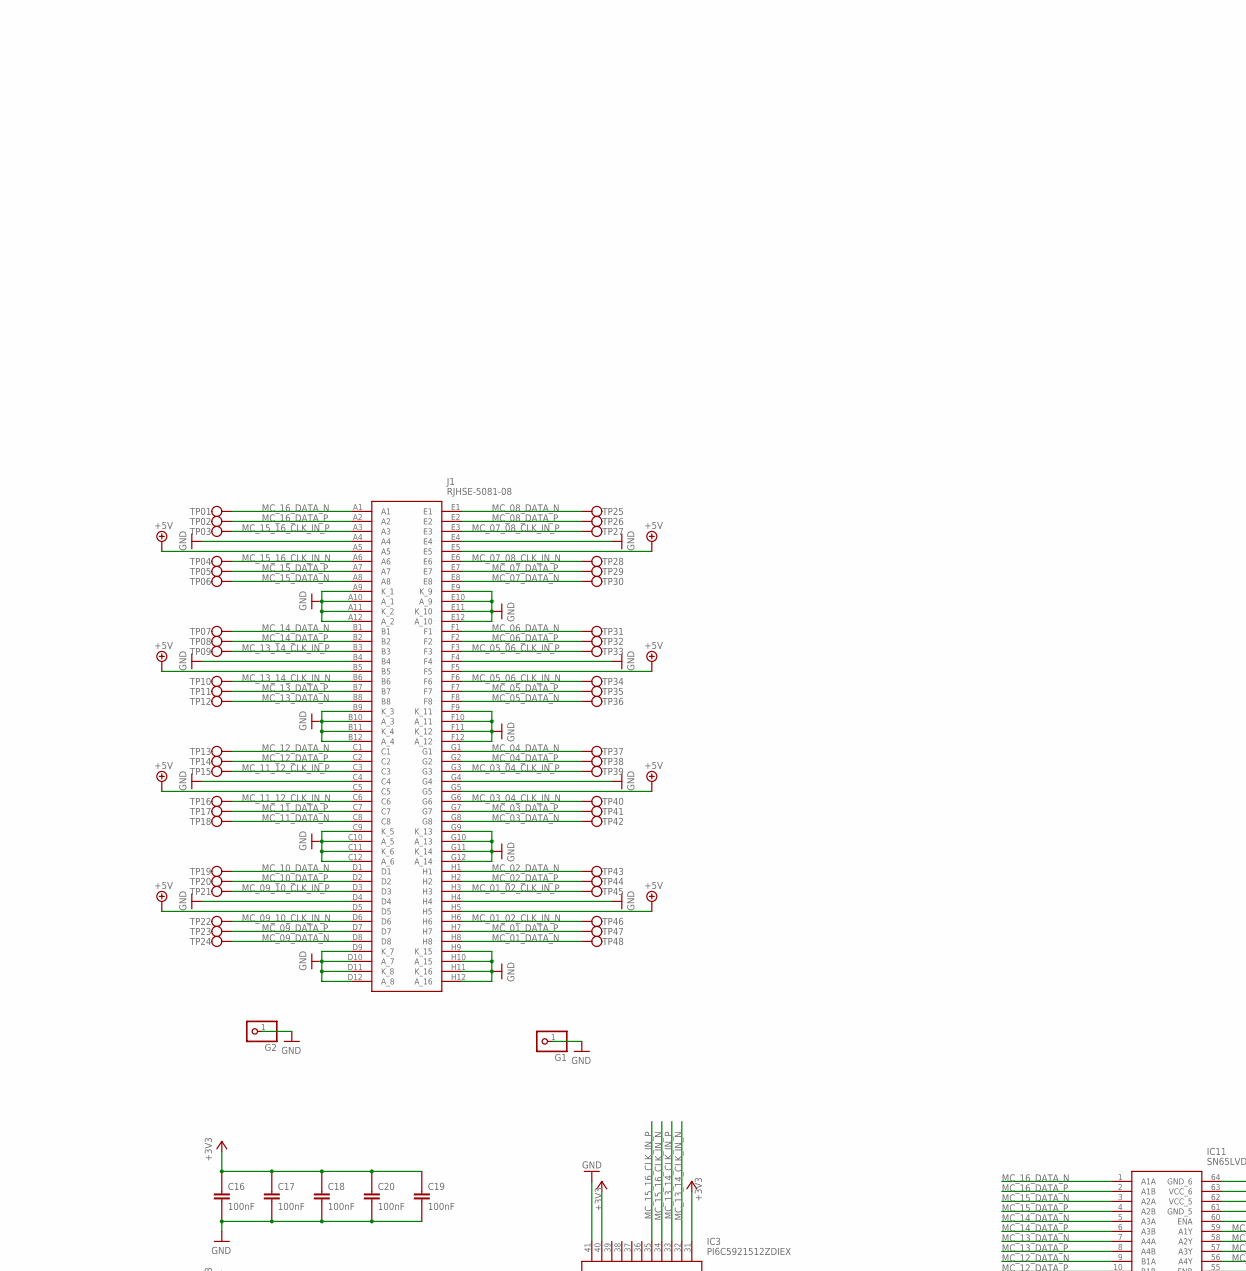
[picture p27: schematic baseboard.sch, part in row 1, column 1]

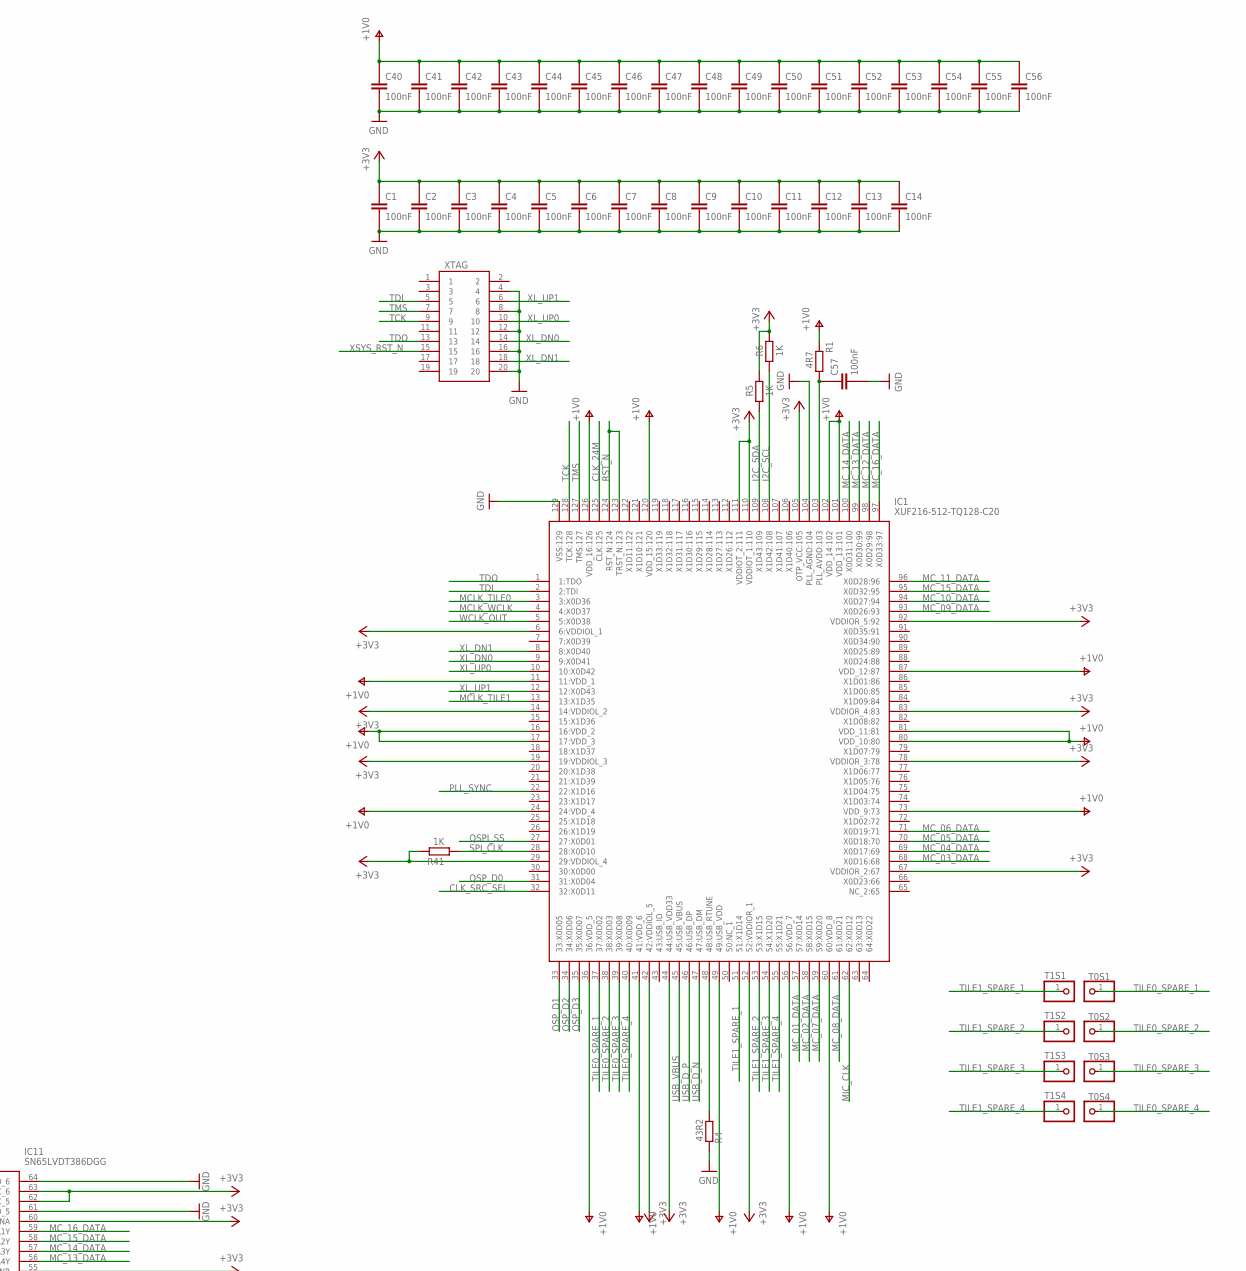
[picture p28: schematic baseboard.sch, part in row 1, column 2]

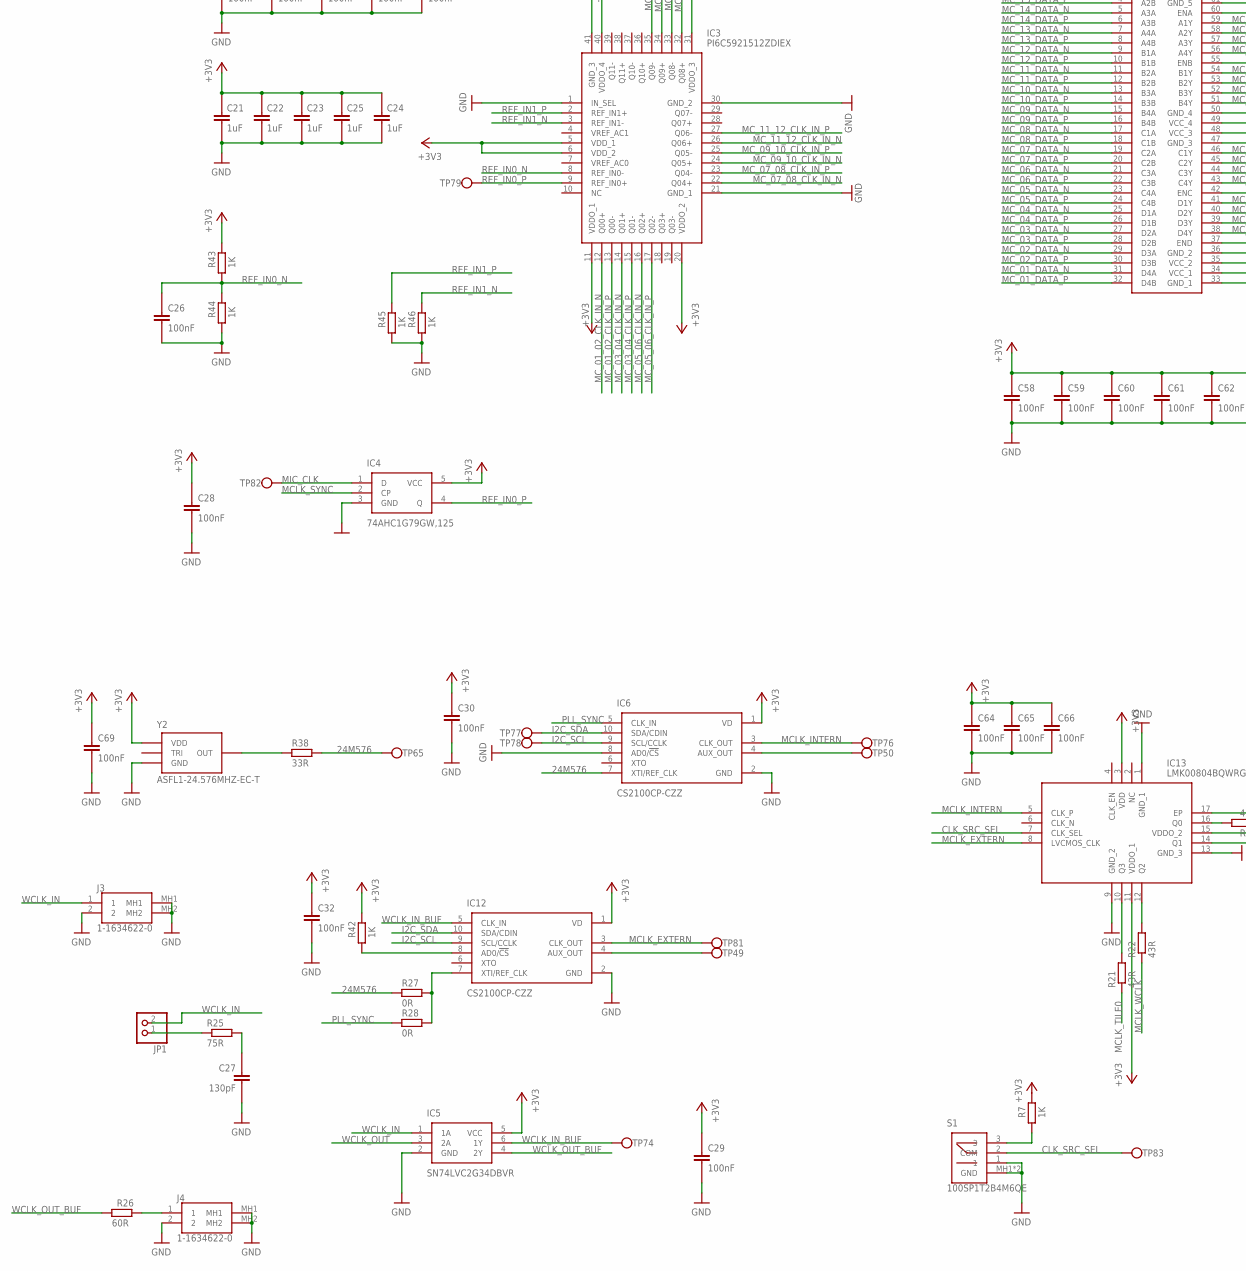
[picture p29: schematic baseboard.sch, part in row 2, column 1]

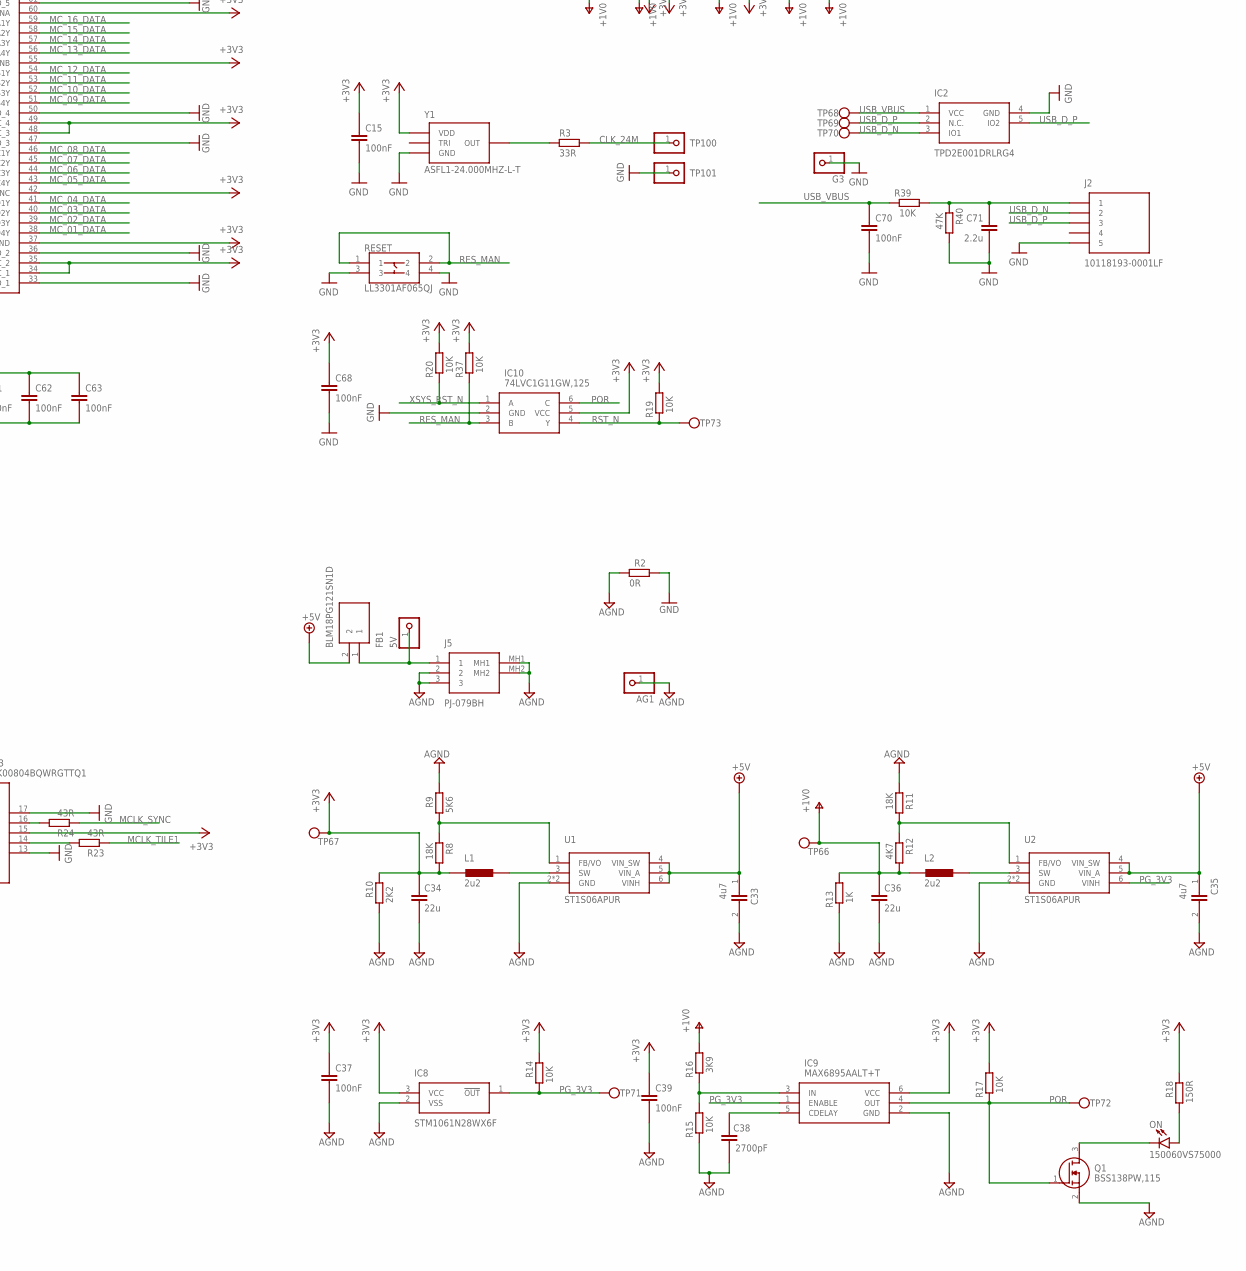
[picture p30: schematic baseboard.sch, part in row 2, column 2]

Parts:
5V: PINHD-1X1; 1X01
AG1: PINHD-1X1; 1X01
C1, C2, C3, C4, C5, C6, C7, C8, C9, C10, C11, C12, C13, C14, C15, C16, C17, C18, C19, C20, C26, C28, C29, C30, C32, C37, C39, C40, C41, C42, C43, C44, C45, C46, C47, C48, C49, C50, C51, C52, C53, C54, C55, C56, C57, C58, C59, C60, C61, C62, C63, C64, C65, C66, C68, C69, C70: 100nF; CAPC1005X55N
C21, C22, C23, C24, C25: 1uF; CAPC1005X55N
C27: 130pF; CAPC1005X55N
C33, C35: 4u7; CAPC1005X55N
C34, C36: 22u; CAPC2012X145N
C38: 2N2; CAPC1005X55N
C71: GRM188R71A225KE15D; CAPC1608X90N
FB1: BLM18PG121SN1D; BEADC1608X95N
G1, G2, G3: PINHD-1X1; 1X01
IC1: XUF216-512-TQ128-C20; QFP40P1600X1600X120-129N
IC2: TPD2E001DRLRG4; SOTFL50P160X60-5N
IC3: PI6C5921512ZDIEX; QFN50P600X600X80-41N
IC4: 74AHC1G79GW,125; SOT65P212X110-5N
IC5: SN74LVC2G34DBVR; SOT95P280X145-6N
IC6, IC12: CS2100CP-CZZ; SOP50P490X110-10N
IC8: STM1061N28WX6F; SOT103P237X112-3N
IC9: MAX6895AALT+T; SON50P100X150X75-6N
IC10: 74LVC1G11GW,125; SOP65P210X110-6N
IC11: SN65LVDT386DGG; SOP50P810X120-64N
IC13: LMK00804BQWRGTTQ1; QFN50P300X300X100-17N
J1: RJHSE-5081-08; RJHSE508108
J2: 10118193-0001LF; 101181930001LF
J3, J4: 1-1634622-0; 116346220
J5: PJ-079BH; PJ079BH
JP1: PINHD-1X2; 1X02
L1, L2: NRH2412T2R2MNGH
ON: 150060VS75000; LEDC1608X80N
Q1: BSS138PW,115; SOT65P210X110-3N
R1: 4R7; RESC1005X40N
R2: 0R; RESC3116X65N
R3, R38: 33R; RESC1005X40N
R4: 43R2; RESC1005X40N
R5, R6, R7, R41, R42, R43, R44, R45, R46: 1K; RESC1005X40N
R8, R11: 18K; RESC2012X65N
R9: 5K6; RESC2012X70N
R10: 2K2; RESC2013X65N
R12: 4K7; RESC2013X65N
R13: AS08J1001ET; RESC2013X65N
R14, R15, R17, R19, R20, R37, R39: 10k; RESC1005X40N
R16: 3K9; RESC0402X15N
R18: 150R; RESC1005X40N
R21, R22, R23, R24: 43R; RESC1005X40N
R25, R26: 75R; RESC1005X40N
R27, R28: CRCW04020000Z0EDC; RESC1005X35N
R40: CRCW040247K0FKEDC; RESC1005X35N
RESET: LL3301AF065QJ; LL3301FF065QJ
S1: 100SP1T2B4M6QE
T0S1, T0S2, T0S3, T0S4, T1S1, T1S2, T1S3, T1S4: PINHD-1X1; 1X01
TP01, TP02, TP03, TP04, TP05, TP06, TP07, TP08, TP09, TP10, TP11, TP12, TP13, TP14, TP15, TP16, TP17, TP18, TP19, TP20, TP21, TP22, TP23, TP24, TP25, TP26, TP27, TP28, TP29, TP30, TP31, TP32, TP33, TP34, TP35, TP36, TP37, TP38, TP39, TP40, TP41, TP42, TP43, TP44, TP45, TP46, TP47, TP48, TP49, TP50, TP65, TP66, TP67, TP68, TP69, TP70, TP71, TP72, TP73, TP74, TP76, TP77, TP78, TP79, TP81, TP82, TP83: TESTPOINT_05_05; TP_05_05
TP100, TP101: PINHD-1X1; 1X01
U1, U2: ST1S06APUR; DFN6D
XTAG: 30320-5002HB; 303205002HB
Y1: ASFL1-24.000MHZ-L-T; ASFL-1
Y2: ASFL1-24.576MHZ-EC-T; ASFL-1

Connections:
24M576: IC6.7 (XTI/REF_CLK), R27.1, R38.2, TP65.TP
+3V3: C1.2, C2.2, C3.2, C4.2, C5.2, C6.2, C7.2, C8.2, C9.2, C10.2, C11.2, C12.2, C13.2, C14.2, C15.2, C16.2, C17.2, C18.2, C19.2, C20.2, C21.2, C22.2, C23.2, C24.2, C25.2, C28.2, C29.2, C30.2, C32.2, C34.2, C37.2, C39.2, C58.2, C59.2, C60.2, C61.2, C62.2, C63.2, C64.2, C65.2, C66.2, C68.2, C69.2, IC1.6 (6:VDDIOL_1), IC1.14 (14:VDDIOL_2), IC1.19 (19:VDDIOL_3), IC1.29 (29:VDDIOL_4), IC1.42 (42:VDDIOL_5), IC1.44 (44:USB_VDD33), IC1.52 (52:VDDIOR_1), IC1.67 (VDDIOR_2:67), IC1.78 (VDDIOR_3:78), IC1.83 (VDDIOR_4:83), IC1.92 (VDDIOR_5:92), IC1.105 (OTP_VCC:105), IC1.110 (VDDIOT_1:110), IC1.111 (VDDIOT_2:111), IC3.5 (VDD_1), IC3.6 (VDD_2), IC3.11 (VDDO_1), IC3.20 (VDDO_2), IC3.31 (VDDO_3), IC3.40 (VDDO_4), IC4.5 (VCC), IC5.5 (VCC), IC6.1 (VD), IC8.3 (VCC), IC9.6 (VCC), IC10.5 (VCC), IC11.34 (VCC_1), IC11.35 (VCC_2), IC11.37 (END), IC11.42 (ENC), IC11.48 (VCC_3), IC11.49 (VCC_4), IC11.55 (ENB), IC11.60 (ENA), IC11.62 (VCC_5), IC11.63 (VCC_6), IC12.1 (VD), IC13.3 (VDD), IC13.11 (VDDO_1), IC13.15 (VDDO_2), L1.1, R5.2, R6.2, R7.2, R8.2, R10.2, R14.2, R17.2, R18.2, R19.2, R20.2, R37.2, R41.2, R42.2, R43.2, TP67.TP, Y1.VDD, Y2.VDD
+5V: C33.1, C35.1, FB1.2, J1.A5, J1.B5, J1.C5, J1.D5, J1.E5, J1.F5, J1.G5, J1.H5, U1.4 (VIN_SW), U1.5 (VIN_A), U1.6 (VINH), U2.4 (VIN_SW), U2.5 (VIN_A)
AGND: AG1.1, C33.2, C34.1, C35.2, C36.1, C37.1, C38.2, C39.1, IC8.2 (VSS), IC9.2 (GND), J5.2, J5.3, J5.MH1, J5.MH2, Q1.2 (S), R2.1, R9.2, R10.1, R11.1, R13.1, R15.1, U1.2 (GND), U1.GND, U2.2 (GND), U2.GND
CLK_24M: IC1.125 (CLK:125), R3.2, TP100.1
CLK_SRC_SEL: IC1.32 (32:X0D11), IC13.7 (CLK_SEL), S1.2 (COM), TP83.TP
GND: C1.1, C2.1, C3.1, C4.1, C5.1, C6.1, C7.1, C8.1, C9.1, C10.1, C11.1, C12.1, C13.1, C14.1, C15.1, C16.1, C17.1, C18.1, C19.1, C20.1, C21.1, C22.1, C23.1, C24.1, C25.1, C26.1, C27.2, C28.1, C29.1, C30.1, C32.1, C40.1, C41.1, C42.1, C43.1, C44.1, C45.1, C46.1, C47.1, C48.1, C49.1, C50.1, C51.1, C52.1, C53.1, C54.1, C55.1, C56.1, C57.1, C58.1, C59.1, C60.1, C61.1, C62.1, C63.1, C64.1, C65.1, C66.1, C68.1, C69.1, C70.1, C71.2, G1.1, G2.1, G3.1, IC1.104 (PLL_AGND:104), IC1.129 (VSS:129), IC2.4 (GND), IC3.1 (IN_SEL), IC3.21 (GND_1), IC3.30 (GND_2), IC3.41 (GND_3), IC4.3 (GND), IC5.2 (GND), IC6.2 (GND), IC6.8 (AD0/!CS), IC10.2 (GND), IC11.33 (GND_1), IC11.36 (GND_2), IC11.47 (GND_3), IC11.50 (GND_4), IC11.61 (GND_5), IC11.64 (GND_6), IC12.2 (GND), IC13.1 (GND_1), IC13.9 (GND_2), IC13.13 (GND_3), IC13.17 (EP), J1.A4, J1.A9 (K_1), J1.A10 (A_1), J1.A11 (K_2), J1.A12 (A_2), J1.B4, J1.B9 (K_3), J1.B10 (A_3), J1.B11 (K_4), J1.B12 (A_4), J1.C4, J1.C9 (K_5), J1.C10 (A_5), J1.C11 (K_6), J1.C12 (A_6), J1.D4, J1.D9 (K_7), J1.D10 (A_7), J1.D11 (K_8), J1.D12 (A_8), J1.E4, J1.E9 (K_9), J1.E10 (A_9), J1.E11 (K_10), J1.E12 (A_10), J1.F4, J1.F9 (K_11), J1.F10 (A_11), J1.F11 (K_12), J1.F12 (A_12), J1.G4, J1.G9 (K_13), J1.G10 (A_13), J1.G11 (K_14), J1.G12 (A_14), J1.H4, J1.H9 (K_15), J1.H10 (A_15), J1.H11 (K_16), J1.H12 (A_16), J2.5, J2.MH1 (5), J2.MH2 (5), J2.MP1 (5), J2.MP2 (5), J2.MP3 (5), J2.MP4 (5), J3.2, J3.MH1, J3.MH2, J4.2, J4.MH1, J4.MH2, R2.2, R4.1, R40.2, R44.1, R45.1, R46.1, RESET.3, RESET.4, S1.1, S1.MH1 (GND), S1.MH2 (GND), TP101.1, XTAG.4, XTAG.8, XTAG.12, XTAG.16, XTAG.20, Y1.GND, Y2.GND
I2C_SCL: IC1.108 (X1D42:108), IC6.9 (SCL/CCLK), IC12.9 (SCL/CCLK), R6.1, TP78.TP
I2C_SDA: IC1.109 (X1D43:109), IC6.10 (SDA/CDIN), IC12.10 (SDA/CDIN), R5.1, TP77.TP
MCLK_EXTERN: IC12.3 (CLK_OUT), IC13.8 (LVCMOS_CLK), TP81.TP
MCLK_INTERN: IC6.3 (CLK_OUT), IC13.5 (CLK_P), TP76.TP
MCLK_SYNC: IC4.2 (CP), R24.1
MCLK_TILE0: IC1.3 (3:X0D36), R21.1
MCLK_TILE1: IC1.13 (13:X1D35), R23.1
MCLK_WCLK: IC1.4 (4:X0D37), R22.1
MC_01_02_CLK_IN_N: IC3.12 (Q00+), J1.H6, TP46.TP
MC_01_02_CLK_IN_P: IC3.13 (Q00-), J1.H3, TP45.TP
MC_01_DATA: IC1.57 (57:X0D14), IC11.38 (D4Y)
MC_01_DATA_N: IC11.31 (D4A), J1.H8, TP48.TP
MC_01_DATA_P: IC11.32 (D4B), J1.H7, TP47.TP
MC_02_DATA: IC1.58 (58:X0D15), IC11.39 (D3Y)
MC_02_DATA_N: IC11.29 (D3A), J1.H1, TP43.TP
MC_02_DATA_P: IC11.30 (D3B), J1.H2, TP44.TP
MC_03_04_CLK_IN_N: IC3.14 (Q01+), J1.G6, TP40.TP
MC_03_04_CLK_IN_P: IC3.15 (Q01-), J1.G3, TP39.TP
MC_03_DATA: IC1.68 (X0D16:68), IC11.40 (D2Y)
MC_03_DATA_N: IC11.27 (D2A), J1.G8, TP42.TP
MC_03_DATA_P: IC11.28 (D2B), J1.G7, TP41.TP
MC_04_DATA: IC1.69 (X0D17:69), IC11.41 (D1Y)
MC_04_DATA_N: IC11.25 (D1A), J1.G1, TP37.TP
MC_04_DATA_P: IC11.26 (D1B), J1.G2, TP38.TP
MC_05_06_CLK_IN_N: IC3.16 (Q02+), J1.F6, TP34.TP
MC_05_06_CLK_IN_P: IC3.17 (Q02-), J1.F3, TP33.TP
MC_05_DATA: IC1.70 (X0D18:70), IC11.43 (C4Y)
MC_05_DATA_N: IC11.23 (C4A), J1.F8, TP36.TP
MC_05_DATA_P: IC11.24 (C4B), J1.F7, TP35.TP
MC_06_DATA: IC1.71 (X0D19:71), IC11.44 (C3Y)
MC_06_DATA_N: IC11.21 (C3A), J1.F1, TP31.TP
MC_06_DATA_P: IC11.22 (C3B), J1.F2, TP32.TP
MC_07_08_CLK_IN_N: IC3.22 (Q04+), J1.E6, TP28.TP
MC_07_08_CLK_IN_P: IC3.23 (Q04-), J1.E3, TP27.TP
MC_07_DATA: IC1.59 (59:X0D20), IC11.45 (C2Y)
MC_07_DATA_N: IC11.19 (C2A), J1.E8, TP30.TP
MC_07_DATA_P: IC11.20 (C2B), J1.E7, TP29.TP
MC_08_DATA: IC1.61 (61:X0D21), IC11.46 (C1Y)
MC_08_DATA_N: IC11.17 (C1A), J1.E1, TP25.TP
MC_08_DATA_P: IC11.18 (C1B), J1.E2, TP26.TP
MC_09_10_CLK_IN_N: IC3.24 (Q05+), J1.D6, TP22.TP
MC_09_10_CLK_IN_P: IC3.25 (Q05-), J1.D3, TP21.TP
MC_09_DATA: IC1.93 (X0D26:93), IC11.51 (B4Y)
MC_09_DATA_N: IC11.15 (B4A), J1.D8, TP24.TP
MC_09_DATA_P: IC11.16 (B4B), J1.D7, TP23.TP
MC_10_DATA: IC1.94 (X0D27:94), IC11.52 (B3Y)
MC_10_DATA_N: IC11.13 (B3A), J1.D1, TP19.TP
MC_10_DATA_P: IC11.14 (B3B), J1.D2, TP20.TP
MC_11_12_CLK_IN_N: IC3.26 (Q06+), J1.C6, TP16.TP
MC_11_12_CLK_IN_P: IC3.27 (Q06-), J1.C3, TP15.TP
MC_11_DATA: IC1.96 (X0D28:96), IC11.53 (B2Y)
MC_11_DATA_N: IC11.11 (B2A), J1.C8, TP18.TP
MC_11_DATA_P: IC11.12 (B2B), J1.C7, TP17.TP
MC_12_DATA: IC1.98 (X0D29:98), IC11.54 (B1Y)
MC_12_DATA_N: IC11.9 (B1A), J1.C1, TP13.TP
MC_12_DATA_P: IC11.10 (B1B), J1.C2, TP14.TP
MC_13_14_CLK_IN_N: IC3.32 (Q08+), J1.B6, TP10.TP
MC_13_14_CLK_IN_P: IC3.33 (Q08-), J1.B3, TP09.TP
MC_13_DATA: IC1.99 (X0D30:99), IC11.56 (A4Y)
MC_13_DATA_N: IC11.7 (A4A), J1.B8, TP12.TP
MC_13_DATA_P: IC11.8 (A4B), J1.B7, TP11.TP
MC_14_DATA: IC1.100 (X0D31:100), IC11.57 (A3Y)
MC_14_DATA_N: IC11.5 (A3A), J1.B1, TP07.TP
MC_14_DATA_P: IC11.6 (A3B), J1.B2, TP08.TP
MC_15_16_CLK_IN_N: IC3.34 (Q09+), J1.A6, TP04.TP
MC_15_16_CLK_IN_P: IC3.35 (Q09-), J1.A3, TP03.TP
MC_15_DATA: IC1.95 (X0D32:95), IC11.58 (A2Y)
MC_15_DATA_N: IC11.3 (A2A), J1.A8, TP06.TP
MC_15_DATA_P: IC11.4 (A2B), J1.A7, TP05.TP
MC_16_DATA: IC1.97 (X0D33:97), IC11.59 (A1Y)
MC_16_DATA_N: IC11.1 (A1A), J1.A1, TP01.TP
MC_16_DATA_P: IC11.2 (A1B), J1.A2, TP02.TP
MIC_CLK: IC1.62 (62:X0D12), IC4.1 (D), TP82.TP
unnamed: IC1.48 (48:USB_RTUNE), R4.2
unnamed: R38.1, Y2.OUT
unnamed: R3.1, Y1.OUT
unnamed: C57.2, IC1.103 (PLL_AVDD:103), R1.2
unnamed: R7.1, S1.3
unnamed: C27.1, R25.2
unnamed: L1.2, U1.3 (SW)
unnamed: R8.1, R9.1, U1.1 (FB/VO)
unnamed: L2.2, U2.3 (SW)
unnamed: IC9.3 (IN), R15.2, R16.1
unnamed: ON.2 (A), R18.1
unnamed: R11.2, R12.1, U2.1 (FB/VO)
unnamed: C38.1, IC9.5 (CDELAY)
unnamed: ON.1 (K), Q1.3 (D)
unnamed: 5V.1, FB1.1, J5.1
unnamed: C71.1, J2.1, R39.2, R40.1
unnamed: IC12.8 (AD0/!CS), R42.1
unnamed: IC12.4 (AUX_OUT), TP49.TP
unnamed: JP1.1, R25.1
unnamed: IC6.4 (AUX_OUT), TP50.TP
unnamed: IC12.7 (XTI/REF_CLK), R27.2, R28.2
unnamed: IC13.16 (Q0), R24.2
unnamed: IC13.14 (Q1), R23.2
unnamed: IC13.12 (Q2), R22.2
unnamed: IC13.10 (Q3), R21.2
unnamed: J4.1, R26.2
PG_3V3: IC8.1 (!OUT), IC9.1 (ENABLE), R14.1, TP71.TP, U2.6 (VINH)
PLL_SYNC: IC1.22 (22:X1D16), IC6.5 (CLK_IN), R28.1
POR: IC9.4 (OUT), IC10.6 (C), Q1.1 (G), R17.1, TP72.TP
QSPI_SS: IC1.27 (27:X0D01)
QSP_D0: IC1.31 (31:X0D04)
QSP_D1: IC1.33 (33:X0D05)
QSP_D2: IC1.34 (34:X0D06)
QSP_D3: IC1.35 (35:X0D07)
REF_IN0_N: C26.2, IC3.8 (REF_IN0-), R43.1, R44.2
REF_IN0_P: IC3.9 (REF_IN0+), IC4.4 (Q), TP79.TP
REF_IN1_N: IC3.3 (REF_IN1-), R46.2
REF_IN1_P: IC3.2 (REF_IN1+), R45.2
RES_MAN: IC10.3 (B), R37.1, RESET.1, RESET.2
RST_N: IC1.123 (TRST_N:123), IC1.124 (RST_N:124), IC10.4 (Y), R19.1, TP73.TP
SPI_CLK: IC1.28 (28:X0D10), R41.1
TCK: IC1.128 (TCK:128), XTAG.9
TDI: IC1.2 (2:TDI), XTAG.5
TDO: IC1.1 (1:TDO), XTAG.13
TILE0_SPARE_1: IC1.37 (37:X0D02), T0S1.1
TILE0_SPARE_2: IC1.38 (38:X0D03), T0S2.1
TILE0_SPARE_3: IC1.39 (39:X0D08), T0S3.1
TILE0_SPARE_4: IC1.40 (40:X0D09), T0S4.1
TILE1_SPARE_1: IC1.51 (51:X1D14), T1S1.1
TILE1_SPARE_2: IC1.53 (53:X1D15), T1S2.1
TILE1_SPARE_3: IC1.54 (54:X1D20), T1S3.1
TILE1_SPARE_4: IC1.55 (55:X1D21), T1S4.1
TMS: IC1.127 (TMS:127), XTAG.7
USB_D_N: IC1.47 (47:USB_DM), IC2.3 (IO1), J2.2, TP70.TP
USB_D_P: IC1.46 (46:USB_DP), IC2.2 (N.C.), IC2.5 (IO2), J2.3, TP69.TP
USB_VBUS: C70.2, IC1.45 (45:USB_VBUS), IC2.1 (VCC), R39.1, TP68.TP
V+: C36.2, C40.2, C41.2, C42.2, C43.2, C44.2, C45.2, C46.2, C47.2, C48.2, C49.2, C50.2, C51.2, C52.2, C53.2, C54.2, C55.2, C56.2, IC1.11 (11:VDD_1), IC1.16 (16:VDD_2), IC1.17 (17:VDD_3), IC1.24 (24:VDD_4), IC1.36 (36:VDD_5), IC1.41 (41:VDD_6), IC1.49 (49:USB_VDD), IC1.56 (56:VDD_7), IC1.60 (60:VDD_8), IC1.73 (VDD_9:73), IC1.80 (VDD_10:80), IC1.81 (VDD_11:81), IC1.87 (VDD_12:87), IC1.101 (VDD_13:101), IC1.102 (VDD_14:102), IC1.120 (VDD_15:120), IC1.126 (VDD_16:126), L2.1, R1.1, R12.2, R13.2, R16.2, TP66.TP
WCLK_IN: IC5.1 (1A), J3.1, JP1.2
WCLK_IN_BUF: IC5.6 (1Y), IC12.5 (CLK_IN), TP74.TP
WCLK_OUT: IC1.5 (5:X0D38), IC5.3 (2A)
WCLK_OUT_BUF: IC5.4 (2Y), R26.1
XL_DN0: IC1.9 (9:X0D41), XTAG.14
XL_DN1: IC1.8 (8:X0D40), XTAG.18
XL_UP0: IC1.10 (10:X0D42), XTAG.10
XL_UP1: IC1.12 (12:X0D43), XTAG.6
XSYS_RST_N: IC10.1 (A), R20.1, XTAG.15

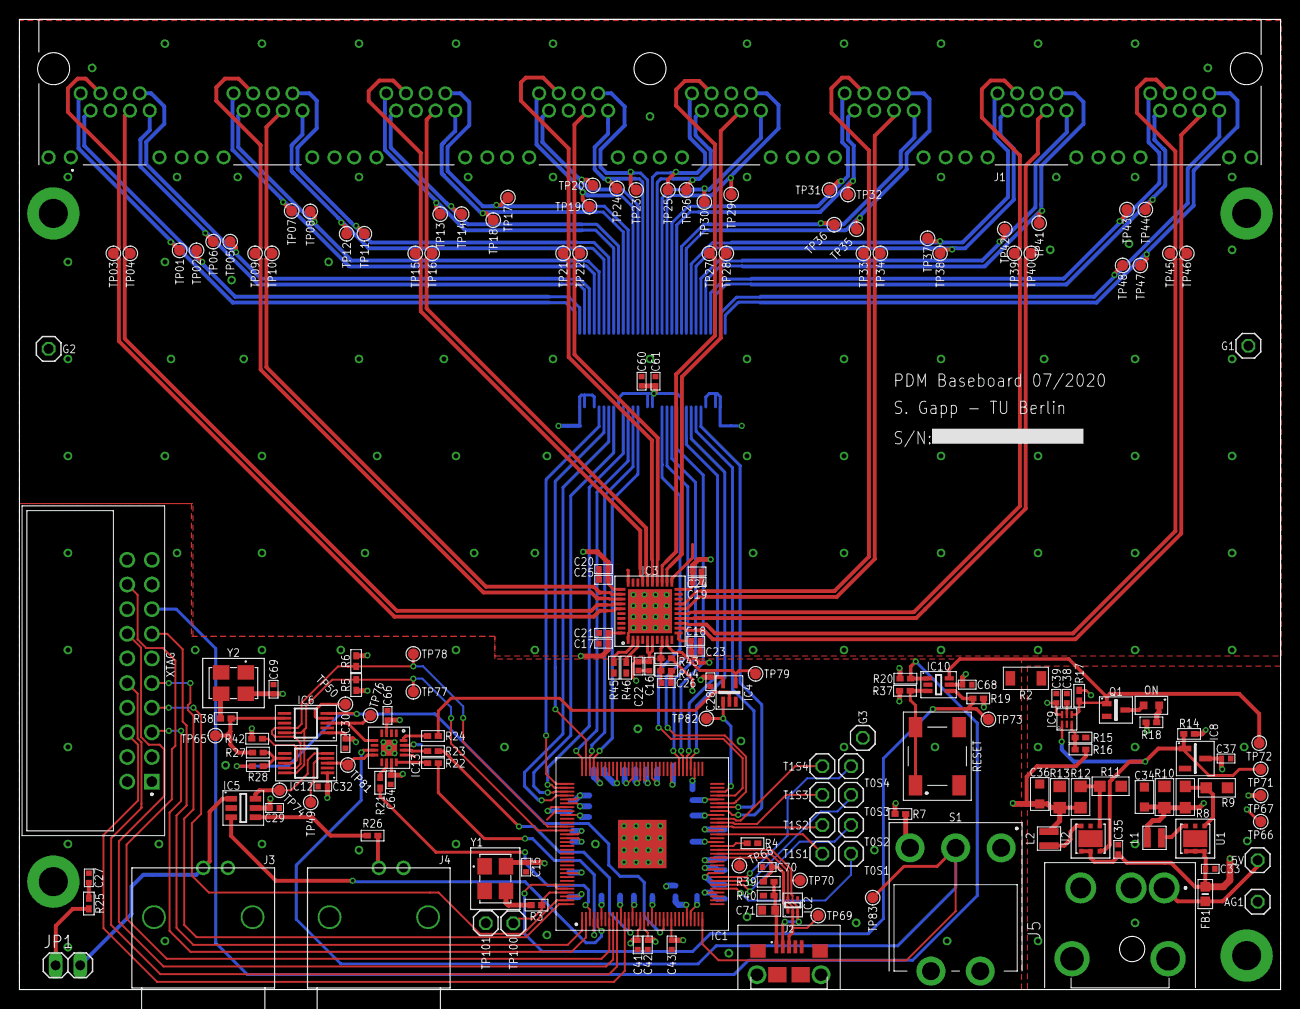
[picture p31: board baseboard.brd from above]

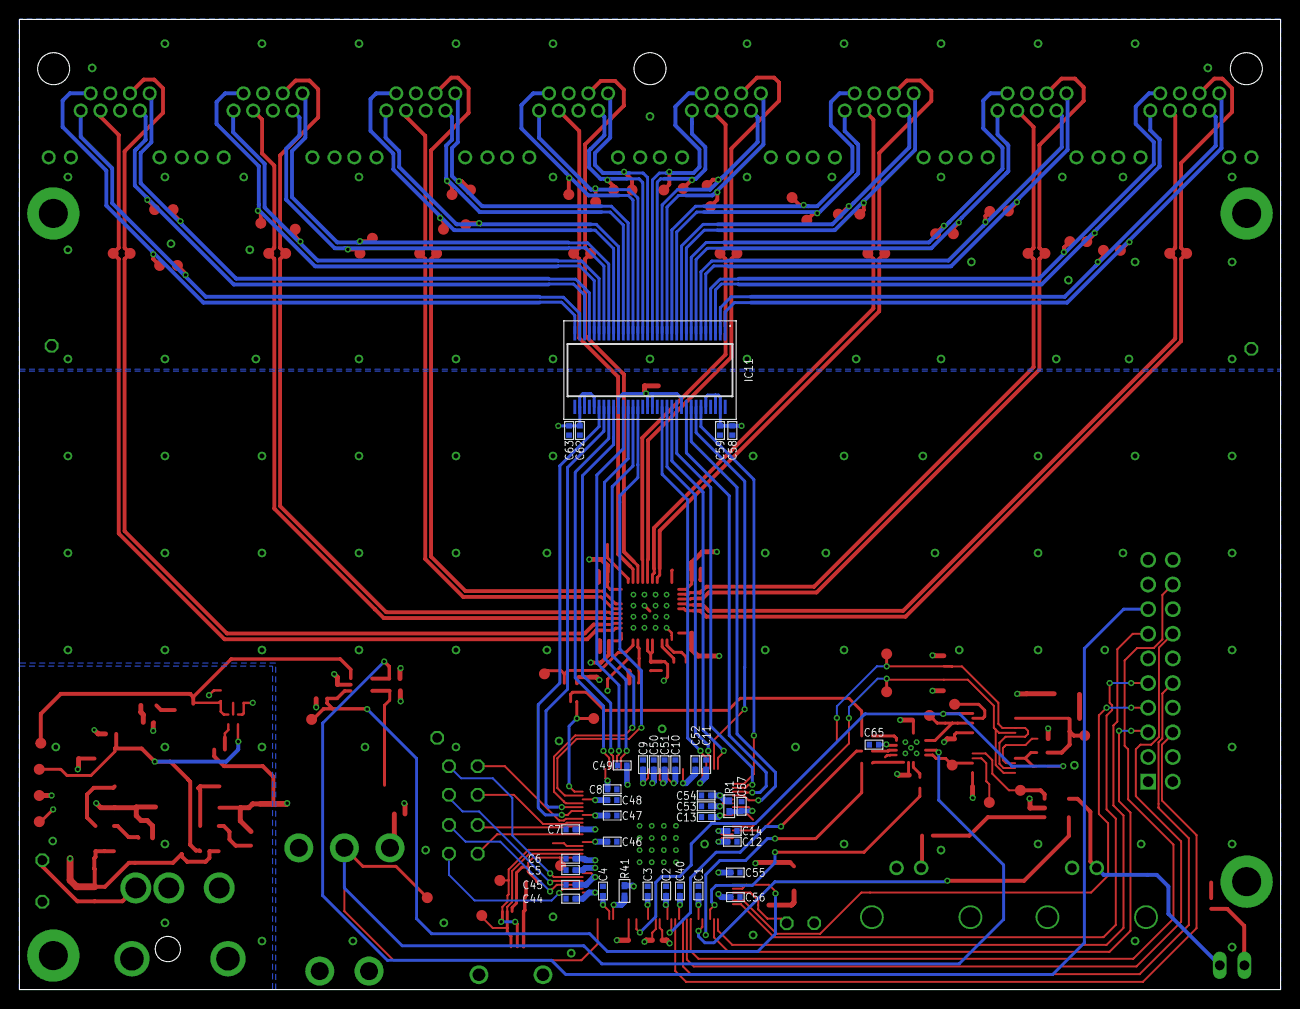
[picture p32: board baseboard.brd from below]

Board: 4 copper layers, 130.0 x 100.0 mm, 219 parts (37 on the bottom side), 141 nets.

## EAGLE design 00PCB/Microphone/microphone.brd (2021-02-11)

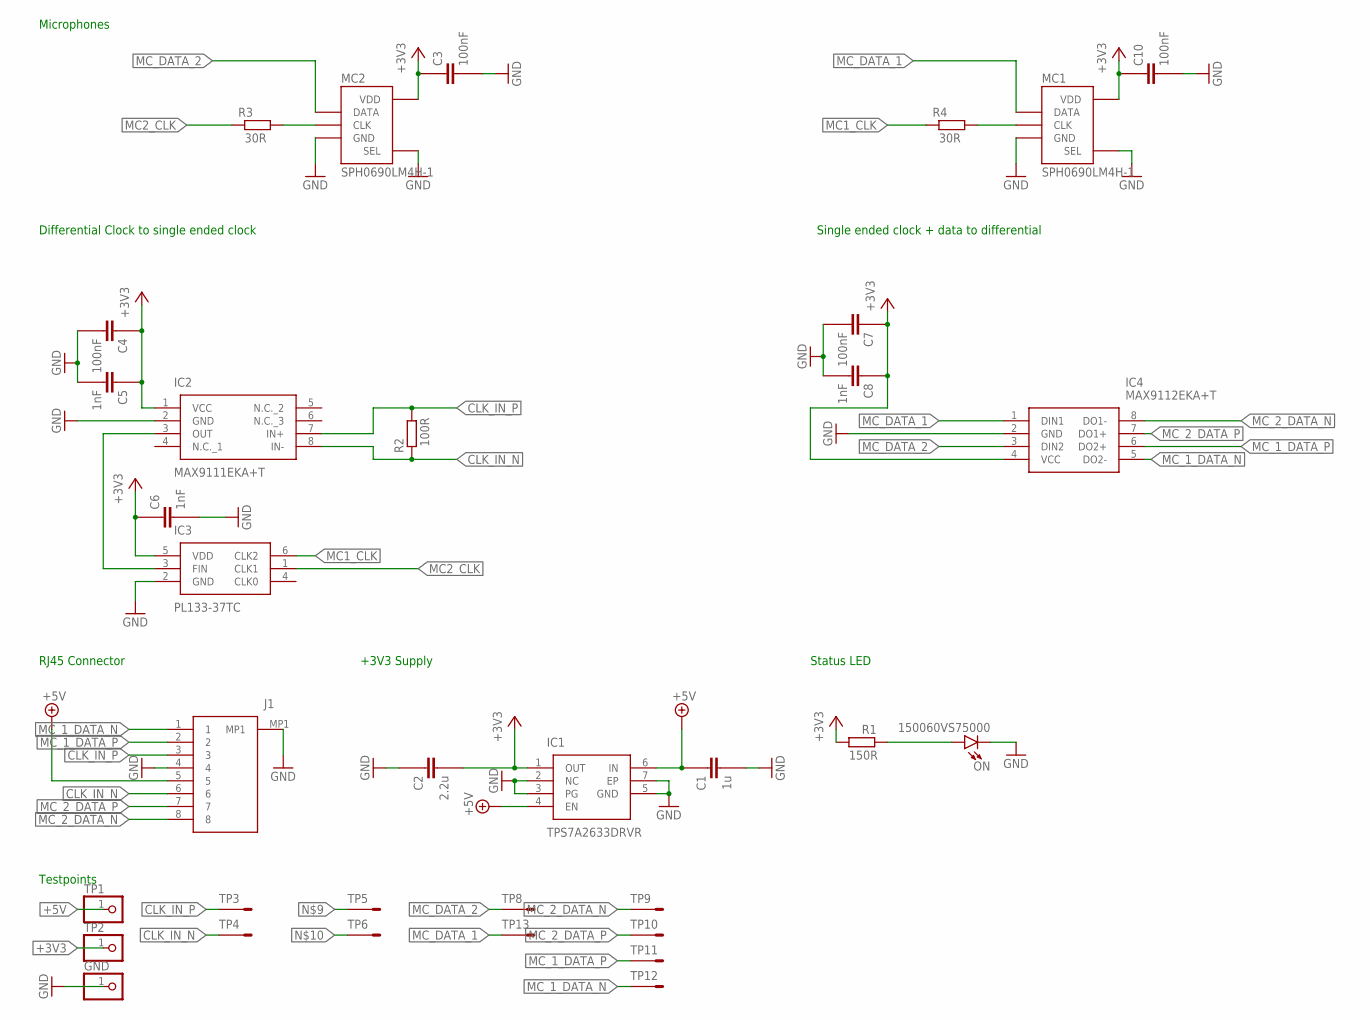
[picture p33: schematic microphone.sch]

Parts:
C1: 1u; CAPC1608X90N
C2: 2.2u; CAPC1608X90N
C3, C4, C7, C10: 100nF; CAPC1005X55N
C5, C6, C8: 1nF; CAPC1005X56N
GND: PINHD-1X1; 1X01
IC1: TPS7A2633DRVR
IC2: MAX9111EKA+T; SOT65P280X145-8N
IC3: PL133-37TC; SOT95P280X135-6N
IC4: MAX9112EKA+T; SOT65P280X145-8N
J1: RJE231883116T
MC1, MC2: SPH0690LM4H-1
ON: 150060VS75000; LEDC1608X80N
R1: 150; RESC1005X40N
R2: RT0402FRE07100RL; RESC1005X8N
R3, R4: 100nF; RESC1005X40N
TP1, TP2: PINHD-1X1; 1X01
TP3, TP4, TP5, TP6, TP8, TP9, TP10, TP11, TP12, TP13: TESTPOINT_05_05; TP_05_05

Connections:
+3V3: C2.2, C3.1, C4.1, C5.1, C6.1, C7.1, C8.1, C10.1, IC1.1 (OUT), IC2.1 (VCC), IC3.5 (VDD), IC4.4 (VCC), MC1.VDD, MC2.VDD, R1.1, TP2.1
+5V: C1.1, IC1.4 (EN), IC1.6 (IN), J1.5, TP1.1
CLK_IN_N: IC2.8 (IN-), J1.6, R2.1, TP4.TP
CLK_IN_P: IC2.7 (IN+), J1.3, R2.2, TP3.TP
GND: C1.2, C2.1, C3.2, C4.2, C5.2, C6.2, C7.2, C8.2, C10.2, GND.1, IC1.2 (NC), IC1.3 (PG), IC1.5 (GND), IC1.7 (EP), IC2.2 (GND), IC3.2 (GND), IC4.2 (GND), J1.4, J1.MP1, MC1.GND, MC1.SEL, MC2.GND, MC2.SEL, ON.1 (K)
MC1_CLK: IC3.6 (CLK2), R4.1
MC2_CLK: IC3.1 (CLK1), R3.1
MC_1_DATA_N: IC4.5 (DO2-), J1.1, TP12.TP
MC_1_DATA_P: IC4.6 (DO2+), J1.2, TP11.TP
MC_2_DATA_N: IC4.8 (DO1-), J1.8, TP9.TP
MC_2_DATA_P: IC4.7 (DO1+), J1.7, TP10.TP
MC_DATA_1: IC4.1 (DIN1), MC1.DATA, TP13.TP
MC_DATA_2: IC4.3 (DIN2), MC2.DATA, TP8.TP
unnamed: ON.2 (A), R1.2
unnamed: IC2.3 (OUT), IC3.3 (FIN)
unnamed: MC2.CLK, R3.2, TP5.TP
unnamed: MC1.CLK, R4.2, TP6.TP

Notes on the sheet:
RJ45 Connector
+3V3 Supply
Differential Clock to single ended clock
Single ended clock + data to differential
Microphones
Status LED
Testpoints

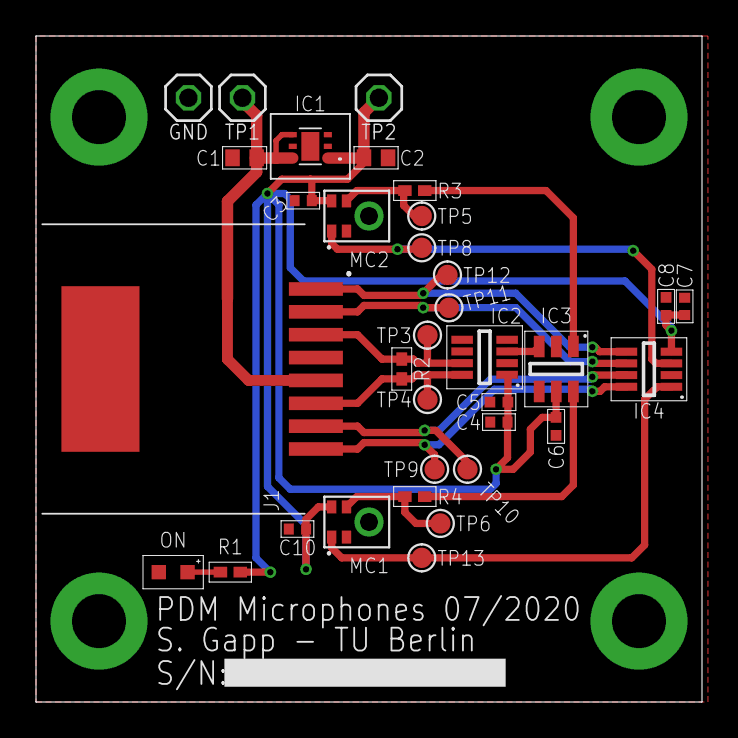
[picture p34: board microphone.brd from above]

Board: 2 copper layers, 37.0 x 37.0 mm, 34 parts (0 on the bottom side), 17 nets.

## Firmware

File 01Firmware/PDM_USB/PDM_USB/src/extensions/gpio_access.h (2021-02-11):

#ifndef _GPIO_ACCESS_H_
#define _GPIO_ACCESS_H_

#include "customdefines.h"

/* General output port bit definitions */
#define P_GPIO_DSD_MODE         (1 << 0) /* DSD mode select 0 = 8i/8o I2S, 1 = 8o DSD*/
#define P_GPIO_DAC_RST_N        (1 << 1)
#define P_GPIO_ADC_RST_N        (1 << 2)
#define P_GPIO_USB_SEL0         (1 << 3)
#define P_GPIO_USB_SEL1         (1 << 4)
#define P_GPIO_VBUS_EN          (1 << 5)
#define P_GPIO_MCLK_FSEL        (1 << 6) /* Select frequency on Phaselink clock. 0 = 24.576MHz for 48k, 1 = 22.5792MHz for 44.1k.*/
#define P_GPIO_PLL_SEL          (1 << 7) /* 1 = CS2100, 0 = Phaselink clock source */

/*LED array defines*/
#define LED_ALL_ON              0xf00f
#define LED_SQUARE_BIG          0x9009
#define LED_SQUARE_SML          0x6006
#define LED_ROW_1               0xf001
#define LED_ROW_2               0xf003
#define LED_ROW_3               0xf007
#define ALL_OFF                 0x0000
// LED array masks
#define LED_MASK_COL_OFF        0x7fff
#define LED_MASK_DISABLE        0xffff

void set_gpio(unsigned bit, unsigned value);
void p_gpio_lock();
void p_gpio_unlock();
unsigned p_gpio_peek();
void p_gpio_out(unsigned x);

#endif

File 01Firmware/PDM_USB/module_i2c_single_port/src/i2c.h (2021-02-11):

// Copyright (c) 2011, XMOS Ltd, All rights reserved
// This software is freely distributable under a derivative of the
// University of Illinois/NCSA Open Source License posted in
// LICENSE.txt and at <http://github.xcore.com/>


#ifndef _i2c_h_
#define _i2c_h_

#ifdef __i2c_conf_h_exists__
#include "i2c_conf.h"
#endif

#include <xs1.h>
#include <xccompat.h>

#ifndef I2C_BIT_TIME

/** This constant defines the time in clock ticks between successive bits.
 * By default set to 1000 for 100 Kbit devices, but it can be overriden to
 * 250 for 400 Kbit devices.
 */
#define I2C_BIT_TIME 10000

#endif

#ifndef SDA_HIGH

/** This constant defines the bit value of a high data bit on the I2C port. The
 * default value is 1, meaning that this is on bit 0 of the port. Set to 2,
 * 4, 8, ... for other bits of the port.
 */
#define SDA_HIGH    128

#endif


#ifndef SCL_HIGH

/** This constant defines the bit value of a high clock on the I2C port. The
 * default value is 2, meaning that this is on bit 1 of the port. Set to 1,
 * 4, 8, ... for other bits of the port.
 */
#define SCL_HIGH    64

#endif


#ifndef S_REST

/** This constant defines the bit value of the other bits of the I2C port.
 * The default value is 0xC, meaning that bits 2 and 3 are kept high. Note
 * that on occassions the other bits are left to float, so external
 * resistors shall be used to reinforce the default value
 */
#define S_REST        0xC

#endif

#ifndef I2C_REPEATED_START_ON_NACK

/** This constant defines the I2C masters behaviour on receipt of a NACK from a busy
 * slave device. By default the issuing of a repeated start is disabled, and the
 * module will ignore NACKs when reading from the device.
 */
#define I2C_REPEATED_START_ON_NACK 0
#endif

#ifndef  I2C_REPEATED_START_MAX_RETRIES

/** This constant defines the maximum number of times the I2C master should issue a
 * repeated start on receipt of a NACK.
 */
#define I2C_REPEATED_START_MAX_RETRIES 10

#endif

#ifndef  I2C_REPEATED_START_DELAY

/** This constant defines the delay in microseconds (us) that the I2C master must wait following
 * the receipt of a NACK before issuing a repeated start.
 */
#define I2C_REPEATED_START_DELAY 500

#endif

/** Struct that holds the data for instantiating the I2C module - it just
 * comprises one port (the clock line and the data line are on the same port),
 * the only other settable parameter is the speed of the bus which is a compile time
 * define.
 */
struct r_i2c {
    port p_i2c;
};

/**Function that initialises the ports on an I2C device.
 *
 * \param i2c Bidirectional port connected to both SDA and SCL.
 */
void i2c_master_init(REFERENCE_PARAM(struct r_i2c, i2cPorts));


/**Function that writes to a register on an I2C device.
 *
 * Note that this function uses the same interface as module_i2c but that
 * the fields master_num and clock_mul are ignored by this function.
 *
 * \param device     Bus address of device, number between 0x00 and 0x7F.
 *
 * \param reg_addr   Address of register to write to, value between 0x00 and 0x7F.
 *
 * \param data       Array where data is stored.
 *
 * \param nbytes     Number of bytes to read and store in data. This parameter
 *                   must be set to '1' and is ignored in this module.
 *                   This parameter is provided for compatibililty with module_i2c_master.
 *
 * \param i2c  Bidirectional port connected to both SDA and SCL.
 */
int i2c_master_write_reg(int device, int reg_addr,
                         const unsigned char data[],
                         int nbytes,
                         REFERENCE_PARAM(struct r_i2c, i2cPorts));

#ifdef __XS2A__
/**Function that reads a register on an I2C device. Supported on XCORE200 only.
 *
 * \param device     Bus address of device, number between 0x00 and 0x7F.
 *
 * \param reg_addr   Address of register to write to, value between 0x00 and 0x7F.
 *
 * \param data       Array where return data will be stored.
 *
 * \param nbytes     Number of bytes to read and store in data. This parameter
 *                   must be set to '1' and is ignored in this module.
 *                   This parameter is provided for compatibililty with module_i2c_master.
 *
 * \param i2c  Bidirectional port connected to both SDA and SCL.
 */
int i2c_master_read_reg(int device, int addr,
                        unsigned char data[],
                        int nbytes,
                        REFERENCE_PARAM(struct r_i2c, i2cPorts));


int i2c_master_rx(int device, unsigned char data[], int nbytes,
        REFERENCE_PARAM(struct r_i2c, i2cPorts));

#endif
#endif
